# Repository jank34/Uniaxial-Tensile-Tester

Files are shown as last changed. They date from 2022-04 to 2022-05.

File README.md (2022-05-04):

# Uniaxial Tensile Tester
1. Repository Contents:

This repository contains the source code and libraries for the functionality of our tensiometer. Moreover, this repository also contains documentations on how to use the Tensiometer, the links on where to buy specific parts used in our Tensiometer, and 3D models for the clamps used in our design.

2. System Parts:

Part 1: Ultrasonic Range Sensor HR-SR04 $4- https://www.adafruit.com/product/4007?gclid=CjwKCAjwsJ6TBhAIEiwAfl4TWK9nOFg9-LFgLM61nsgyrghF30-v_zp0_7Xuo74gRQpIhaaqX7Zv8hoCigkQAvD_BwE

Part 2: Load Cell 20kg SEN-14729 $4- https://www.adafruit.com/product/4543

Part 3: Amplifier HX711 $2.10- https://www.amazon.com/dp/B00XRRNCOO/ref=cm_sw_r_sms_api_glt_i_WRGSQCYD8AA2CNPMWQPD

Part 4: Microcontoller Ard. Uno $15- https://www.amazon.com/Arduino-A000066-ARDUINO-UNO-R3/dp/B008GRTSV6/ref=asc_df_B008GRTSV6/?tag=hyprod-20&linkCode=df0&hvadid=309751315916&hvpos=&hvnetw=g&hvrand=6527864430974582771&hvpone=&hvptwo=&hvqmt=&hvdev=c&hvdvcmdl=&hvlocint=&hvlocphy=1022672&hvtargid=pla-457497319401&psc=1&tag=&ref=&adgrpid=67183599252&hvpone=&hvptwo=&hvadid=309751315916&hvpos=&hvnetw=g&hvrand=6527864430974582771&hvqmt=&hvdev=c&hvdvcmdl=&hvlocint=&hvlocphy=1022672&hvtargid=pla-457497319401

Part 5: LCD Screen With I2C TWI 1602 LCD $5 (pack of 2)- https://www.amazon.com/SunFounder-Serial-Module-Display-Arduino/dp/B019K5X53O/ref=asc_df_B019K5X53O/tag=hyprod-20&linkCode=df0&hvadid=312760964359&hvpos=&hvnetw=g&hvrand=703658664021823897&hvpone=&hvptwo=&hvqmt=&hvdev=c&hvdvcmdl=&hvlocint=&hvlocphy=1022672&hvtargid=pla-563014027379&psc=1

Part 6: Ratchet Crank Crank $26- https://www.amazon.com/CURT-29423-Manual-Trailer-Capacity/dp/B00TU7KME8/ref=sr_1_1?crid=5FC2MYGSWBAJ&keywords=curt+crank&qid=1651167054&s=industrial&sprefix=curt+crank%2Cindustrial%2C47&sr=1-1

Part 7: Pulleys $24- https://www.amazon.com/Chiloskit-Bearing-Bearings-Lifting-Triangular/dp/B07W1X5LTQ/ref=sr_1_25?crid=KAOX3XFYAL91&keywords=mounted%2Bpulley&qid=1651167187&sprefix=mounted%2Bpulley%2Caps%2C69&sr=8-25&th=1

Part 8: 6 feet Metal Cable $2- https://selkirkmetals.com/products/16-gauge-stainless-steel-rebar-tie-wire/?attribute_size=1+lb+Coil+(USA)+%5B304+Grade%5D+%5BQuantity%3A+1%5D&gclid=Cj0KCQjwyMiTBhDKARIsAAJ-9VuQNZg25S4BjEAm6hNkfRDY8u8t7IPsF_znqv66WN3v-eRoYqYu2UMaAg69EALw_wcB

3. Software Dependencies: 

Special libraries for codes in the library folder in the repository.

4. 3D Models:

Misc file contains 3D models of the clamps used in the project.

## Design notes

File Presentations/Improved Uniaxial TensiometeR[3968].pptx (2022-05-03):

## Improved Uniaxial TensiometeR

## Key components

- Ratchet Crank
- Pulleys
- Metal Rope
- LCD Screen
- 3D Printed Clamps

## Advantages of the system

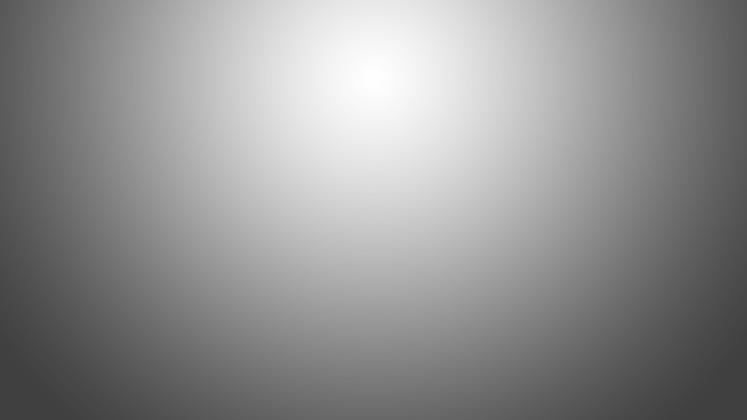
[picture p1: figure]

- Cost effectiveness.
- User friendly.
- Easily Replaceable parts.
- Easy Calibration process
- Accurate and Reliable results.

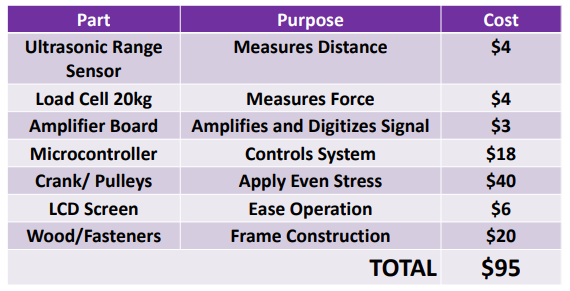
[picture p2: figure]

## System evolution

Initial Design and Results:

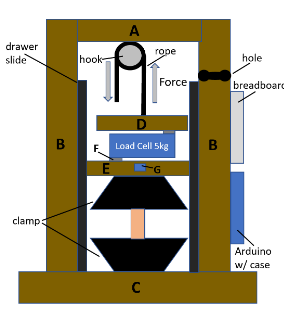
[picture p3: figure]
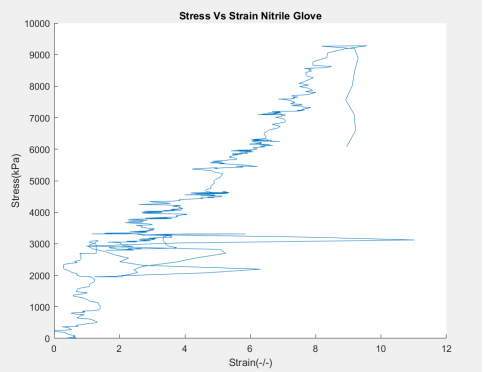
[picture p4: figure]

## System evolution

Modified Design and Results:

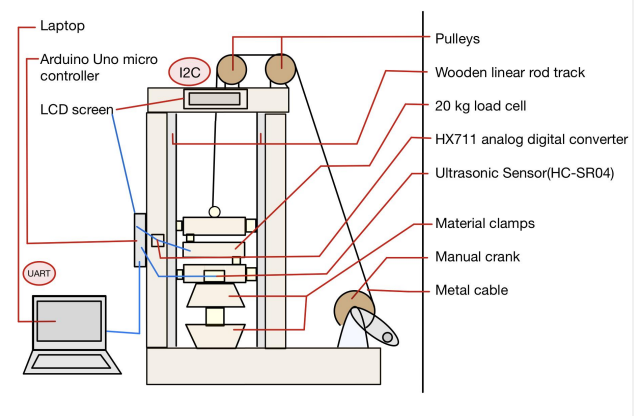
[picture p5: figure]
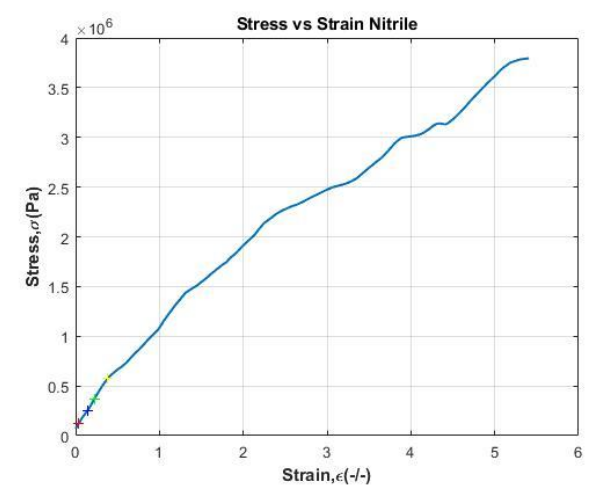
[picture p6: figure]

## Evolution

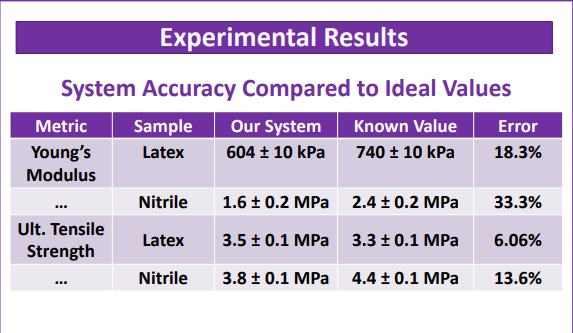
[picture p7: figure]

## Avenues for improvement

- Data Analysis that does not depend on MATLAB
- Additional 3D printed components
- Data retrieval independent of computer connection
- Smaller footprint
- Better sensors
- Taller linear track for more elastic materials

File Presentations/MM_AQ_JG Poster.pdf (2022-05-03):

# Improved Tensiometer

## Abdullah Qureshi, Jan Galia, Max Manier

### Department of Electrical & Computer Engineering, University at Albany

### Problem Statement

- The University at Albany’s chemistry department, as part of their educational mission, intends to build a laboratory for undergraduate students where they can gain hands on experience testing various material properties (including tensile strength). However, due to the extremely high cost of commercial products they have been unable to equip such a laboratory.
- The goal of this project is to build an accurate, low cost, easy to use uniaxial tensile strength tester to support this educational mission.

### System Requirements

### Experimental Results

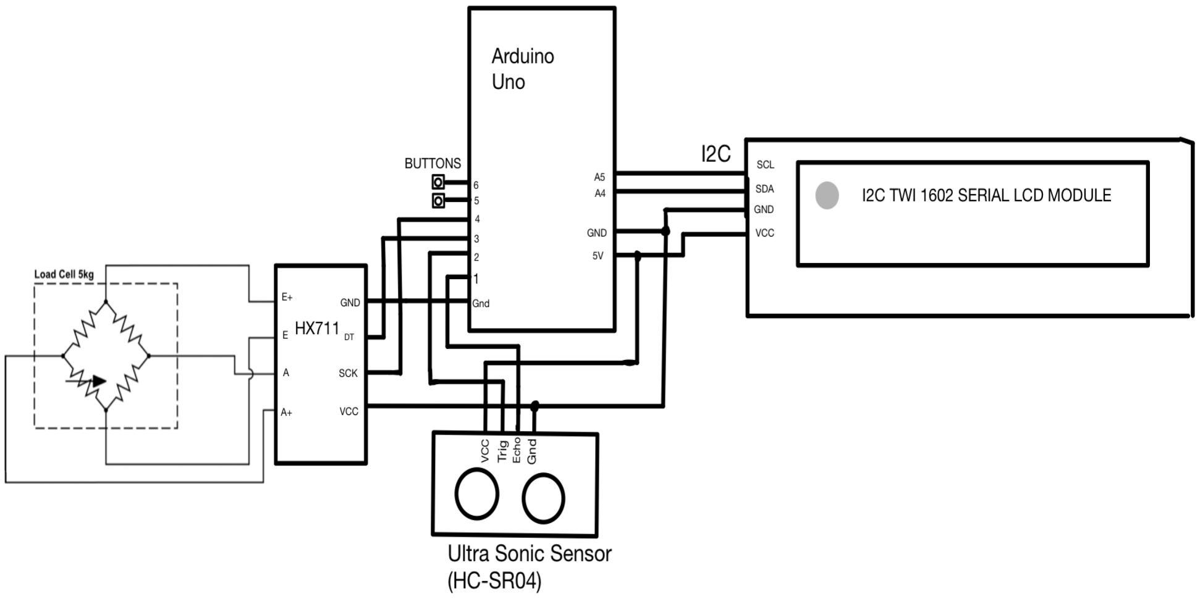
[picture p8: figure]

### Project Partners

### System Design

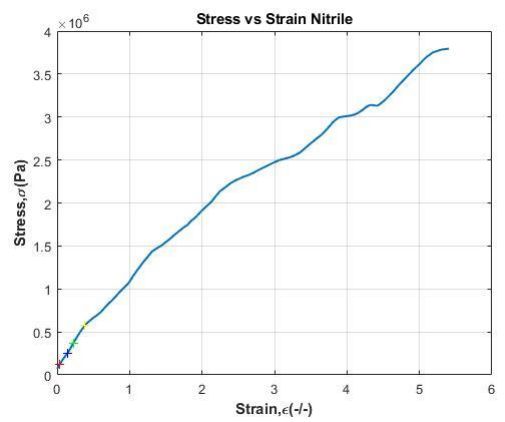
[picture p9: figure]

### System Components & Budget

Metric | Sample | Our System | Known Value | Error
Young’s Modulus | Latex | 604 ± 10 kPa | 740 ± 10 kPa | 18.3%
… | Nitrile | 1.6 ± 0.2 MPa | 2.4 ± 0.2 MPa | 33.3%
Ult. Tensile Strength | Latex | 3.5 ± 0.1 MPa | 3.3 ± 0.1 MPa | 6.06%
… | Nitrile | 3.8 ± 0.1 MPa | 4.4 ± 0.1 MPa | 13.6%
Part | Purpose | Cost
Ultrasonic Range Sensor | Measures Distance | $4
Load Cell 20kg | Measures Force | $4
Amplifier Board | Amplifies and Digitizes Signal | $3
Microcontroller | Controls System | $18
Crank/ Pulleys | Apply Even Stress | $40
LCD Screen | Ease Operation | $6
Wood/Fasteners | Frame Construction | $20
TOTAL | | $95

System Accuracy Compared to Ideal Values

Stress-Strain Curve Produced by Our Tensiometer
- System Accuracy: The system should be able to accurately measure the stress-strain curve, such that Young’s Modulus and Ultimate Tensile Strength can be calculated to within two significant figures.
- System Ease-of-Use: The system should be easy to calibrate and operate by undergraduate students without requiring knowledge of electronics or software programming.

Key System Features
The following features were implemented to satisfy the system requirements:
- Item #1: Inexpensive linear guide rail
- Item #2: Hand crank and pulleys to apply uniform force
- Item #3: LCD screen to provide clear information and useful instructions
- Item #4: Durable design using sturdy materials and manual components
- Item #5: Intuitive easy to use material clamps

Physical Model

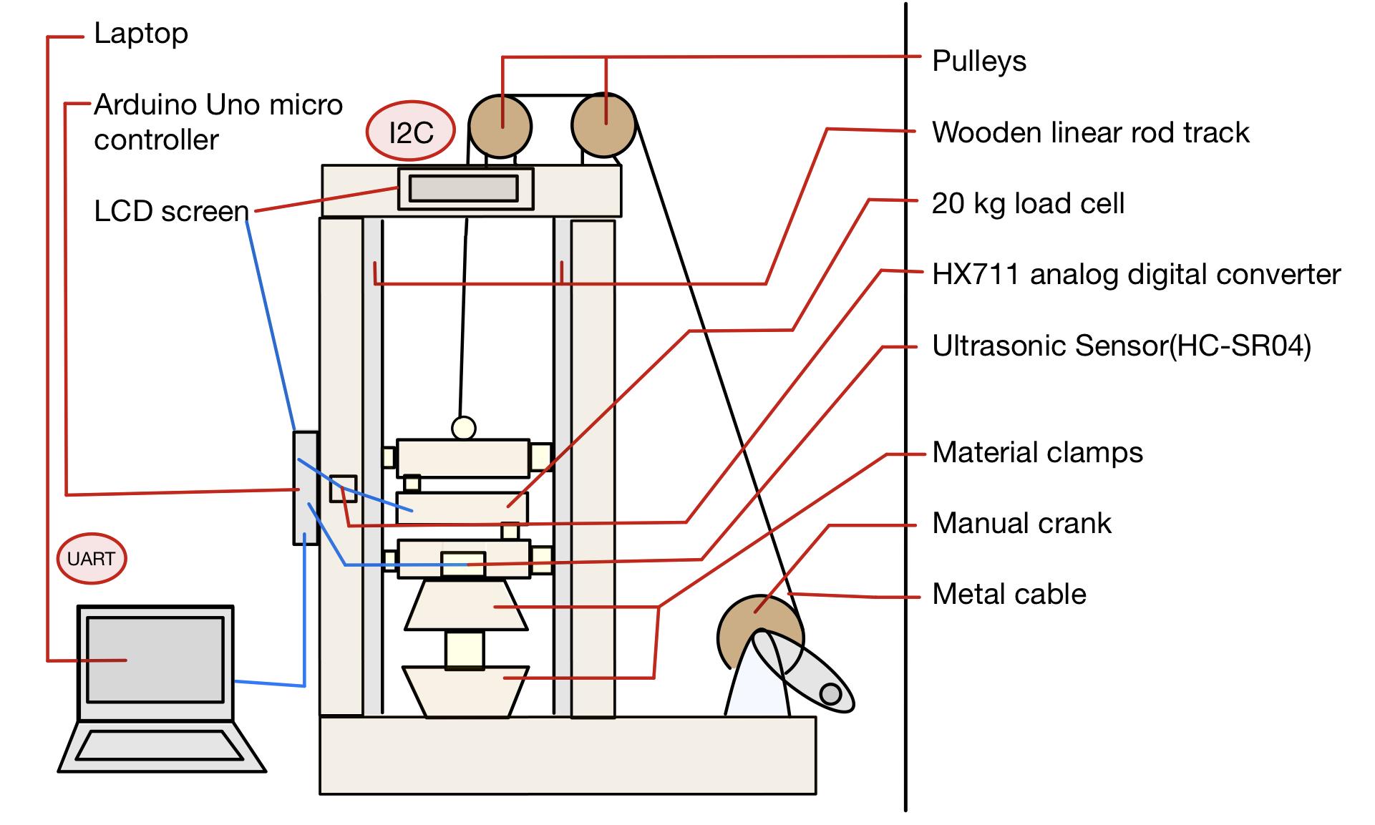
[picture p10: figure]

Circuit Schematic

- Special thanks for Professor Chen, Feldblyun, Yeung, and the University at Albany’s Chemistry Department for sponsoring this project.
- This project was developed in ECE442: Systems Analysis & Design in the Electrical & Computer Engineering Department.

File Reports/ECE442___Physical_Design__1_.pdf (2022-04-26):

PP-2017 V2.1

PHYSICAL DESIGN | 1

# Physical Design Proposal Team 2

Jan Karl Galia, Abdullah Qureshi, Max Manier

Activity Report

✦

### 1 PROPOSED SOLUTION

The proposed design is simplistic in nature and follows the designs constraints. The system consists of sturdy wooden frame and uses two pulleys to efficiently transfer force from an adjacent crank to apply a vertical load. The lower clamp is attached to the base and the upper clamp is attached to the shuttle with the load cell. The material under observation will be placed between these clamps. The laser sensor attached to the shuttle will measure the distance from the base as the rope is pulled through the pulley. The data will be read by both the load sensor and range sensor through micro-controller and processed accordingly. The LCD screen will display commands to help the calibration process and operation of the device. Commands can range from calibration instructions to operation instructions like ”Pull” or ”Stop”.

### 2 SYSTEM ARCHITECTURE

The main focus of the proposed design is to add a crank in order to apply a vertical load. In order to add a crank two pulleys have to be added on top of the device in order to have a linear and uniform pulling force on the shuttle.

- Jan Karl Galia,
E-mail: jgalia@albany.edu,
- Abdullah Qureshi,
E-mail: aqureshi@albany.edu,
- Max Manier,
E-mail: mmanier@albany.edu, University at Albany.

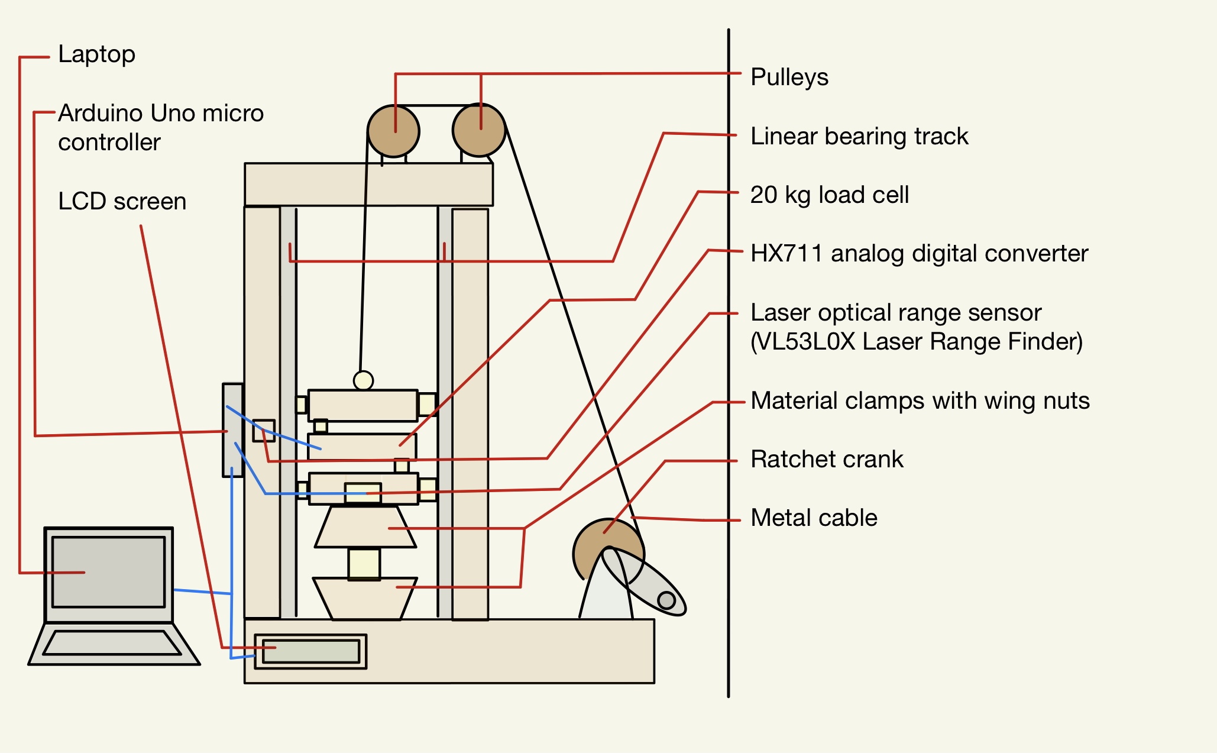
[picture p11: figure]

Figure 1. Current state of the tensiometer physical design.

Figure 1 depicts the current system physical design with a crank for applying a vertical load, and pulleys for linear force implementation on shuttle. The system also consists of LCD screen in order to aid in the calibration process and provide user with operation instructions.
The addition of the LCD screen will change the circuitry of the system. Figure 2 depicts the current system circuitry with the load cell acting a wheatstone bridge and the resulting output voltage amplified to the range of the ADC. The HX711 board uses the amplifed value to perform a ADC conversion and then communicates the results using the I2C communication standard with the attached microcontroller. Figure 3 depicts Arduino and LCD schematic. The LCD screen also uses the I2C communication standard with the attached microcontroller in order to make circuitry and wire management easier. The LCD screen typically uses 16 pins to

Activity Report

2 | PHYSICAL DESIGN

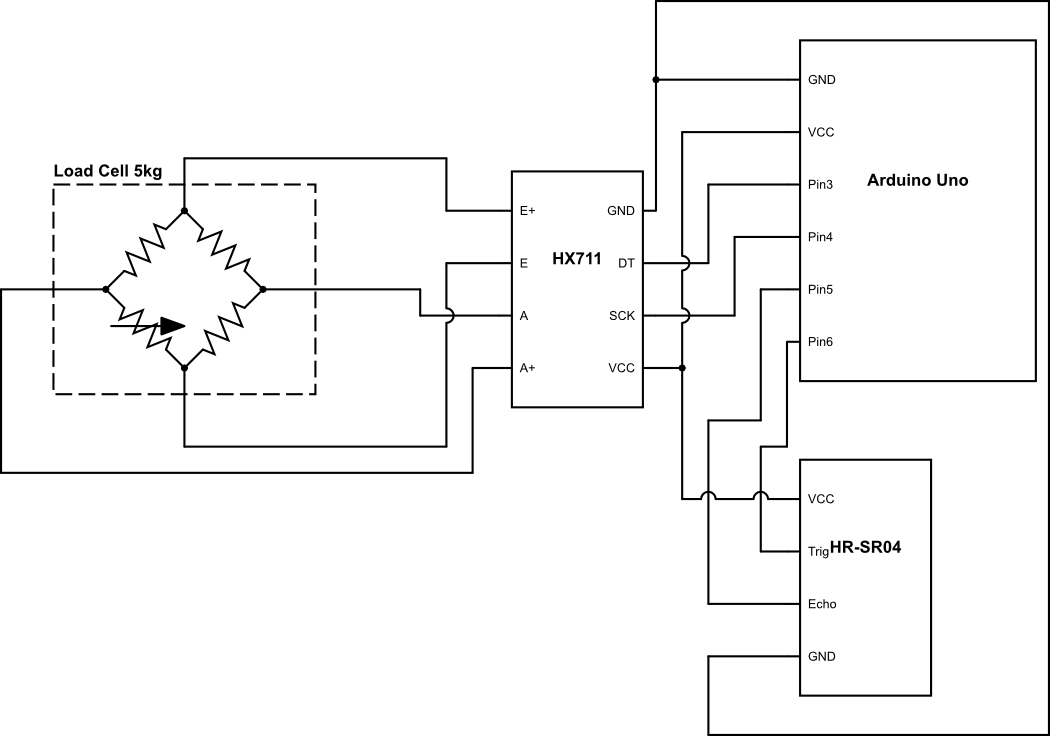
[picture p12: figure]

Figure 2. Schematic diagram of tensiometer electronics.

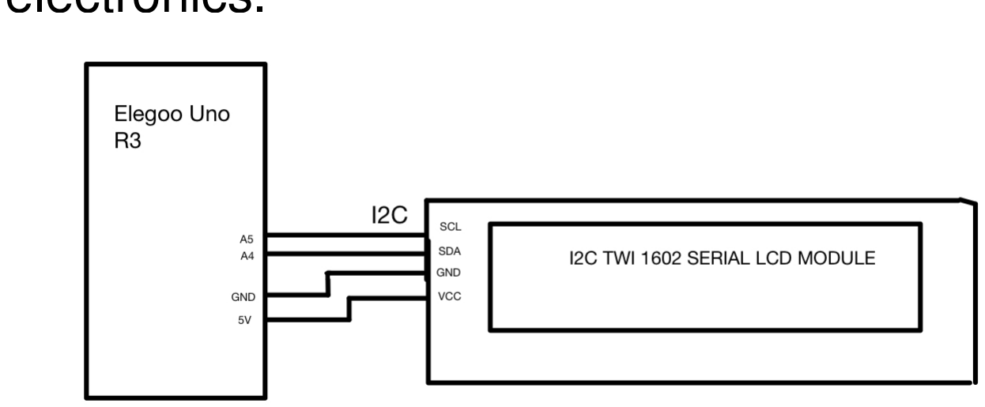
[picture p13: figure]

Figure 3. Schematic diagram of LCD screen With I2C.

work and display data on it, but by sing the I2C communication standard it can be reduced to 4 pins as shown in Figure 2. The LCD can work only by using pin VCC for power, SDA pin for data transmission, SCL pin for clock signal, GND pin for ground.

### 2.1 System Components

Some of the problems with the old system included non uniform application of force on the material under observation due to pulling the rope by hand. It was decided by the the team to use a Ratchet crank to pull the rope for uniform application of force, and because of its ability to stop the shuttle from returning to its original position. The following improvement has potential to greatly improve the accuracy, precision, and ease of use of the tensiometer. In order to have the crank apply linear force it was decided by the team to add pulleys onto the system. Another problem with the old system included the elasticity of the rope being used. It was decided by the team to replace that

Item | Part # | Cost
Ultrasonic Range Sensor | HR-SR04 | $4
Load Cell 20kg | SEN-14729 | $12
Amplifier | HX711 | $10
Microcontoller | Ard. Uno | $15
LCD Screen With I2C | TWI 1602 LCD | $5
Ratchet Crank | Crank | $20
Pulleys | Pulley | $20
Metal Cable | Cable | $3
TOTAL | | $89
Table 1
Table 1 displays an overview of parts purchased and their estimated price.

with a metal cable to reduce uncertainty in the data collection. Moreover, in order to reduce human error the team decided to use an LCD to display commands to help with the calibration process and operation of the device. Following are the new components of the system.

2.1.1 Ratchet Crank

The Ratchet Crank allows a user to apply uniform force on the material being stretched, and enables the user to stop the shuttle from going back to its original position without the need of force being applied from the user.

2.1.2 Pulleys

Pulleys are used in order to make the crank apply linear force on the material being stretched, and enables smooth pulling mechanism because of reduction in friction.

2.1.3 Metal Cable

The Metal Cable has negligible elasticity which reduces the errors and uncertainties in the data collected and the final result of Young’s Modulus and Ultimate Tensile Strength.

2.1.4 LCD Screen with I2C

The LCD screen will display commands to help the calibration process and operation of the device. Commands can range from calibration instructions to operation instructions like ”Pull” or ”Stop”.

PP-2017 V2.1

SURNAME et al. | 3

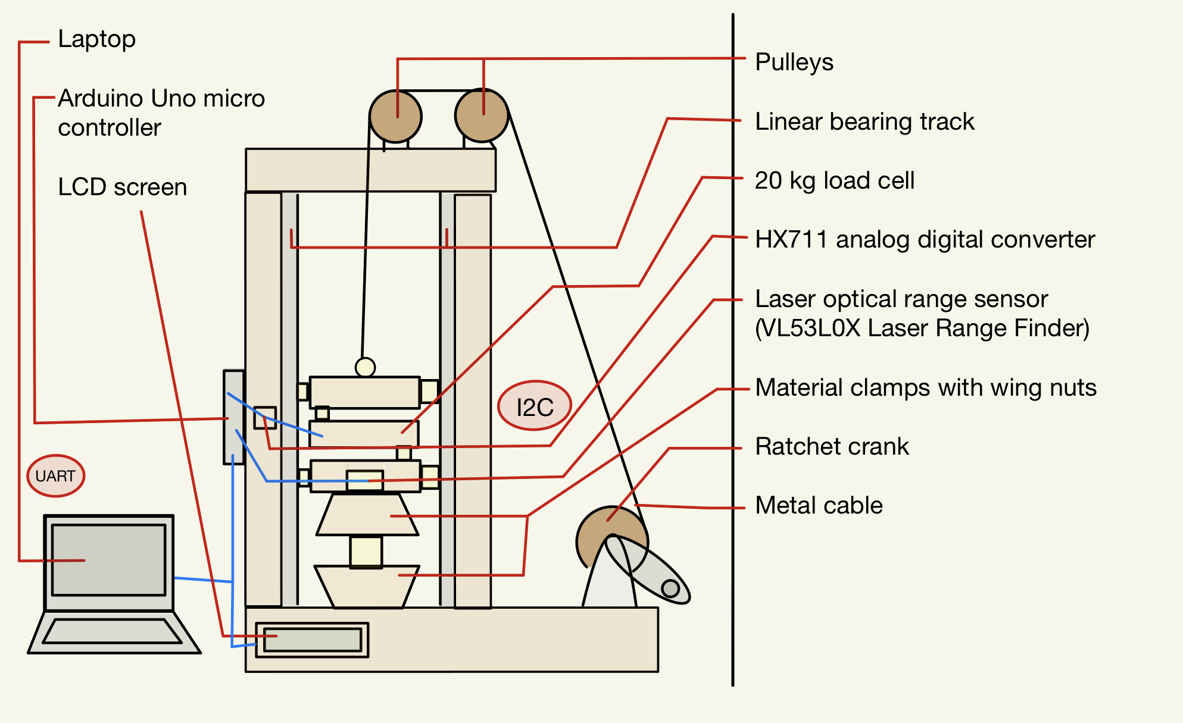
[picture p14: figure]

Figure 4. The current tensiometer system implements two communication standards (protocol) I2C and UART.

### 2.2 Engineering Standards

The current system utilizes I2C and UART protocols. I2C protocol is a serial communication protocol in which data is transferred bit by bit along a single wire (the SDA line). UART stands for Universal Asynchronous Receiver/Transmitter. It’s not a communication protocol like I2C, but a physical circuit in a microcontroller. A UART’s main purpose is to transmit and receive serial data.

2.2.1 I2C Protocol
I2C uses two wires to transmit data between devices. The current Tensiometer design uses Arduiono Uno which contains only one SCL (Pin 5) and SDA (Pin 4) pin. These same pins are connected to HX711, HR-SR04, and LCD screen. The SDA pin sends and receives data to and from the sensors and the LCD screen. SCK pin only sends a clock signal to the sensors and LCD screen to indicate data transmission and completion in data transmission.

2.2.2 UART Protocol
The main purpose of UART protocol is to send and receive data. The current Tensiometer design uses Arduino Uno which uses UART protocol to transmit and receive data to and from user’s laptop. In order for the communication to work the user must set the baud rate in the code. Any speed up to 115200 baud is viable but current code uses 9600 baud speed.

2.2.3 Data Standards
The current Tensiometer design uses Ardu Plotter tool in order to upload data calculated from the load cell and distance sensor to a CSV file. The data form CSV file is then uploaded to Matlab for creating stress vs strain curve, and calculate Young’s Modulus and Ultimate Tensile Strength.

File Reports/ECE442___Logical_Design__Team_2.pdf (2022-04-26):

PP-2017 V2.1

ANALYSIS & LOGICAL DESIGN | 1

# Uniaxial Tensile Tester Team 2

Jan Karl F. Galia, Max J. Manier, Abdullah A. Qureshi

Activity Report

Abstract—Among the problems with the current tensiometer design are accuracy of the range sensor, friction between the track, weight limit of the load cell, elasticity of the cable for pulling, human error when pulling, and non-uniform force application. The problems described above need to be addressed because they add errors to the measurements, making it difficult to calculate Young’s Modulus and Ultimate Tensile Strength accurately. The fixes for these problems include: Replacing the current range sensor with a laser optical range sensor for relatively accurate measurements of strain. Replacing the current load cell with a 20-kilogram load cell allows greater force application when stressing materials with large Young’s Modulus. Replacing the current pulling track with a linear bearing track reduces measurement errors caused by resistance. Replacing current cable with non elastic metal cable reduces errors in measurements caused by rope elasticity. Adding a ratchet crank in order to apply force uniformly. Lastly, adding a LCD screen to prompt the users with basic instructions improves ease of use. These solutions will allow for the stress and strain to be measured with greater accuracy and consistency.

Index Terms—Uniaxial Tensiometer, System Analysis, Engineering Design

✦

### 1 BACKGROUND

A tensiometer tests the strength and elasticity of a material by applying stress and observing how the material stretches, deforms, and eventually breaks. In order to accurately measure these variables both a load cell that measures the force applied, and a range sensor to find the amount the material stretches are necessary. It is essential that these sensors be calibrated and that the system allows for uniform and steady application of force. Any significant deviation of values will result in an inaccurate representation of material properties. The operation of this device should be relatively easy to learn and consistent in its performance regardless of the operator.
The current prototype [1] has several problem areas that have been identified. The range
- Jan Karl Galia,
E-mail: jgalia@albany.edu,
- Max Manier,
E-mail: mmanier@albany.edu,
- Abdullah Qureshi,
E-mail: aqureshi@albany.edu, University at Albany.

sensor is unreliable, it often produces inaccurate or even random values. There is significant friction between the track and shuttle which produces additional stress on the load sensor thereby inflating stress values. The weight limit of the load cell is fairly limited and will not allow for the testing of stronger materials. There is elasticity in the rope used to apply force and its own tensile properties could impact measurements. Testing has shown high potential for human error when applying force. The operator can easily unintentionally apply force at an uneven rate or even reduce force applied. The current system does not allow for a uniform increase in application of force. Lastly the code is cumbersome to use, especially for those unfamiliar with basic programming.
In order to improve upon the design several components will be replaced and some components will be added. The range sensor can be replaced with a laser range sensor rated for a higher degree of accuracy. The current track is a drawer slider and replacing it with a guide rail that uses bearings could reduce friction and weight of the shuttle. The load cell can be replaced with a 20kg load cell with the

Activity Report

2 | ANALYSIS & LOGICAL DESIGN

same dimensions. Instead of using a rope to
apply stress, a metal cable’s tensile properties
would be negligible at these weights. To provide smoother application of force the cable will be run over a pulley to a ratchet crank. Including a LCD screen with instructions can ease use of the device and reduce human error. None of these inclusions are expensive and their costs are comparable to the parts they replace. These modifications however have the potential to greatly increase the overall performance of the system by reducing the errors in measurement of Young’s Modulus and Ultimate Tensile Strength of the material being tested. Making the system more accurate and reliable is essential for the desired functionality of the Stakeholder. The proposed modifications will also make the operation of the devices easier which ultimately helps in operation and consistency of results.

### 2 SYSTEM REQUIREMENTS & CON-

STRAINTS
In order to define requirements it is important to understand what the stakeholder wants. The first major requirement is that the measurement of Young’s Modulus and Ultimate Tensile Strength is relatively equal to the theoretical value, and the system should be able to perform the task with consistency. The second major requirement is that the data collecting components of the system have the ability to be calibrated in order to get accurate and precise measurements for different materials. Calibration also assures similar reliable results across different devices.

### 2.1 Accuracy and Precision

The ”Run Tensile Test” use case aligns with this requirement. The desired functionality of this requirement is to get accurate and precise measurement of stress applied to the material under observation and strain produced in the material due to the application of stress. In order to start, the user will upload the Arduino code and open Ardu Plotter tool from the tools tab. The Ardu Plotter will give the distance of the sensor from the base and the amount of force applied on the material being stretched. The user will use the crank to pull the material until the material breaks. The Ardu Plotter tool will upload the data to an excel sheet which the user will use to plot stress vs. strain curve. Normal Flow
- Step #1: User Loads material to be tested into the clamps and increases tension until material is just taught, but not stressed.
- Step #2: User slowly cranks pulley when LCD displays ”GO”, straining the material.
- Step #3: System records displacement and force every 0.5 seconds.
- Step #4: User stops cranking the rope after the material fractures, can not be displaced further, or LCD displays ”STOP”.
- Step #5: Chemist analyzes the data. Stress is calculated by dividing force by crosssectional area. Stress-strain curve is defined. Material properties are determined. Alternative Flow
- Step #1: User slowly cranks pulley when LCD displays ”GO”, straining the material
- Step #2: Ultimate tensile strength of the material is beyond load cell limits. When load cell approaches 75 percent of maximum load, LEDs flash, and LCD displays warning message.
- Step #3: User stops cranking the rope after the material fractures, can not be displaced further, or LCD displays ”STOP”

### 2.2 Calibration

The ”Calibrate Instrument” use case aligns with this requirement. The desired functionality of this requirement is to calibrate the load cell and the range sensor to get accurate measurement of the force applied on the load cell due to pulling the rope and and strain produced in the material due to application of stress. In order to start the calibration, the user will upload the Arduino code which will prompt the user to put a known load on the load cell and prompt the user to type in raw value of load cell. The code will then generate a calibration value and calibrate the load cell to give an accurate measurement of the load. Normal Flow

PP-2017 V2.1

SURNAME et al. | 3

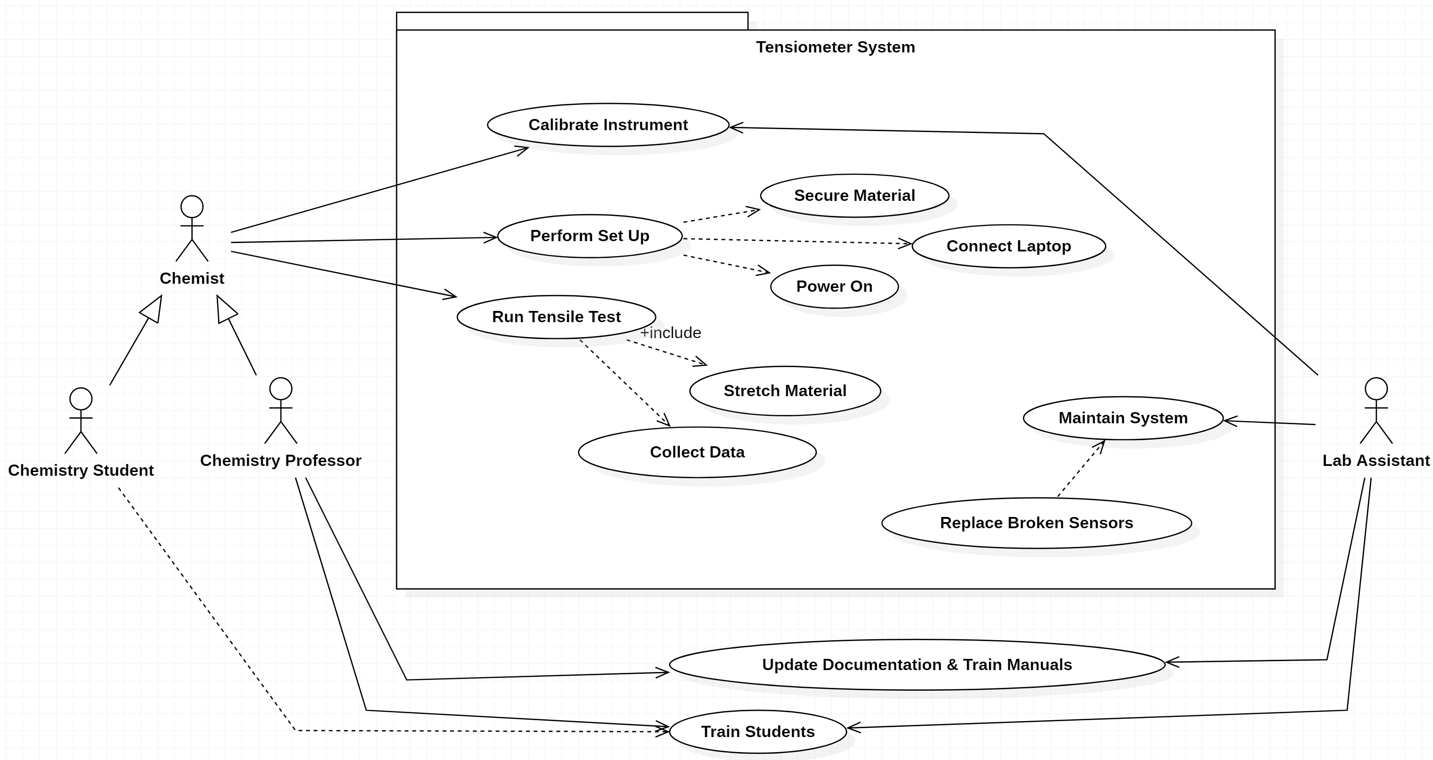
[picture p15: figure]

Figure 1. Use case model of the tensiometer system depicting system actors and the desire actions the system is required to support.

- Step #1: User will upload the Arduino
Code.
- Step #2: Code will prompt the user to put a known load cell.
- Step #3: Code will prompt the user to write the mass of load.
- Step #4: The load cell gets calibrated and the user gets accurate and reliable measurement.
Alternative Flow
- Step #1: User will upload the code.
- Step #2: Code will prompt the user to put a known load cell.
- Step #3: If calibration fails LCD displays warning message.
- Step #4:User re-uploads the code and calibration runs again.

### 2.3 Constraints

System constraints include:
- Time Constraint: Completed and read to presentation/demonstrate by April 22nd
- Budget: Cost needs to be below $150. Going over budget will require strong justification as to the value added from the cost overrun.
- Replication: Relatively straight-forward process to replicate your work, such that we can build out a lab of identical tensiometers.
- Accessibility of Parts: Parts need to be readily accessible, ship quickly (not on back order) and available from common part suppliers (e.g., Digikey, Mouser, Adafruit, SparkFun, Amazon). Avoid parts that are difficult to source.
- Safety: System must be safe to operate without significant training or supervision

### 3 LOGICAL DESIGN

The proposed design is simplistic in nature and follows the designs constraints. Referencing the Figure 2, the system consists of sturdy wooden frame and uses two pulleys to efficiently transfer force from an adjacent crank to apply a vertical load. The lower clamp is attached to the base and the upper clamp is attached to the shuttle with the load cell. The material under observation will be placed between these

Activity Report

4 | ANALYSIS & LOGICAL DESIGN


Figure 2. Uniaxial Tensile Tester Design

clamps. The laser sensor attached to the shuttle will measure the distance from the base as the rope is pulled through the pulley. The data will be read by both the load sensor and range sensor through micro-controller and processed accordingly. The LCD screen will display commands to help the calibration process and operation of the device. Commands can range from calibration instructions to operation instructions like ”Pull” or ”Stop”.

### 3.1 Design Justification

This design is better than potential alternatives because of its ability to increase the load uniformly, low friction linear bearing tracks, higher load capacity, useful LCD screen, and easy-to-use clamps. This design allows for intuitive operation and accurate values. The current system is cumbersome to use and does not provide accurate and precise measurements of stress and strain. These shortfalls will impede the users ability to find Young’s Modulus and Ultimate Tensile Strength of the material under observation. The advancements stated above will increase the accuracy and precision of measurements by reducing systematic and human errors.

REFERENCES

[1] J. H. Arrizabalaga, A. D. Simmons, and M. U. Nollert, “Fabrication of an economical arduino-based uniaxial tensile tester,” Journal of Chemical Education, vol. 94, no. 4, pp. 530–533, 2017. [Online]. Available: https: //doi.org/10.1021/acs.jchemed.6b00639

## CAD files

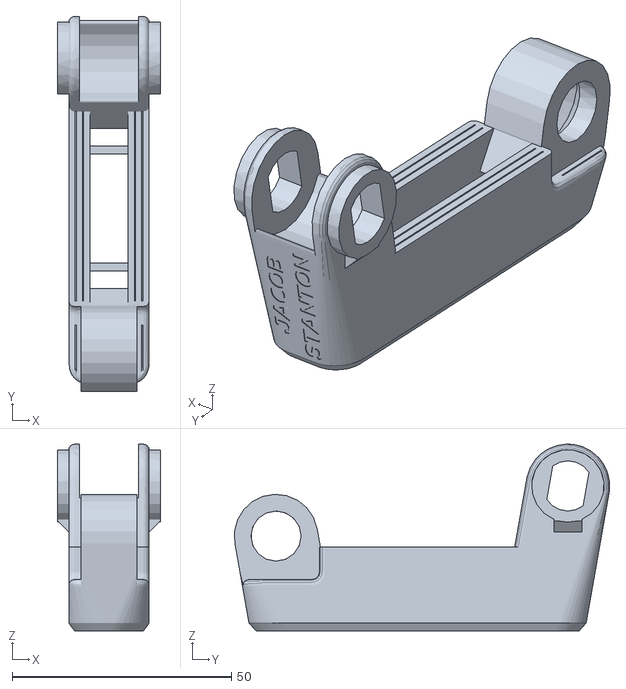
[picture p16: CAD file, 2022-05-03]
MISC/jawBottom(1).STL
23.4 x 85.4 x 42.5

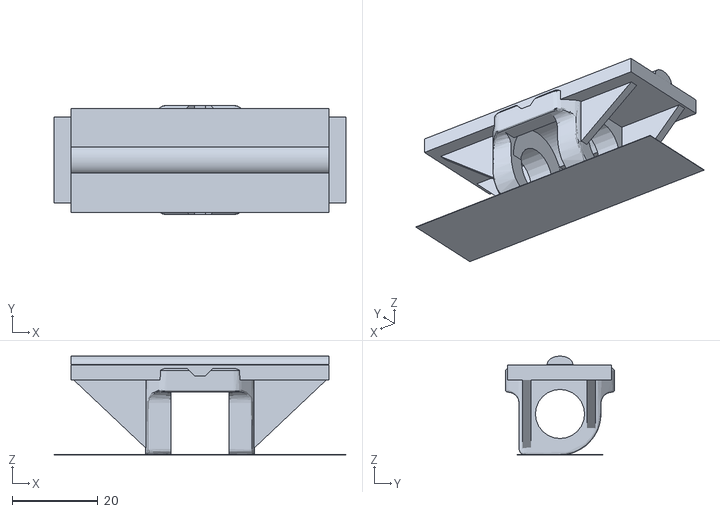
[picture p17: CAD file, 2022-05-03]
MISC/Pad Male(7).stl
68.0 x 25.4 x 23.0

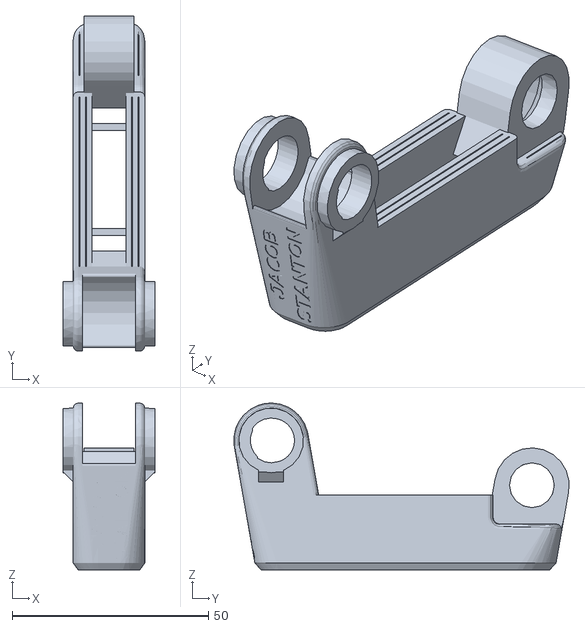
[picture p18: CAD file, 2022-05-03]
MISC/lower jaw(4).stl
23.4 x 85.4 x 42.5

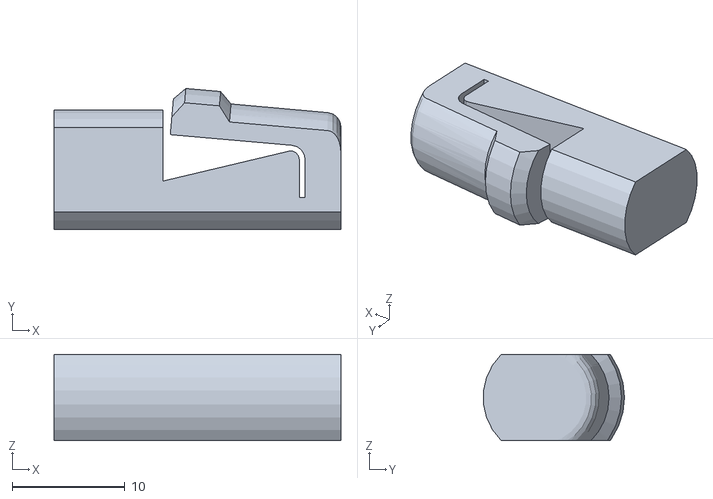
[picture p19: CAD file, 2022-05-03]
MISC/pin(8).STL
25.4 x 12.5 x 7.62

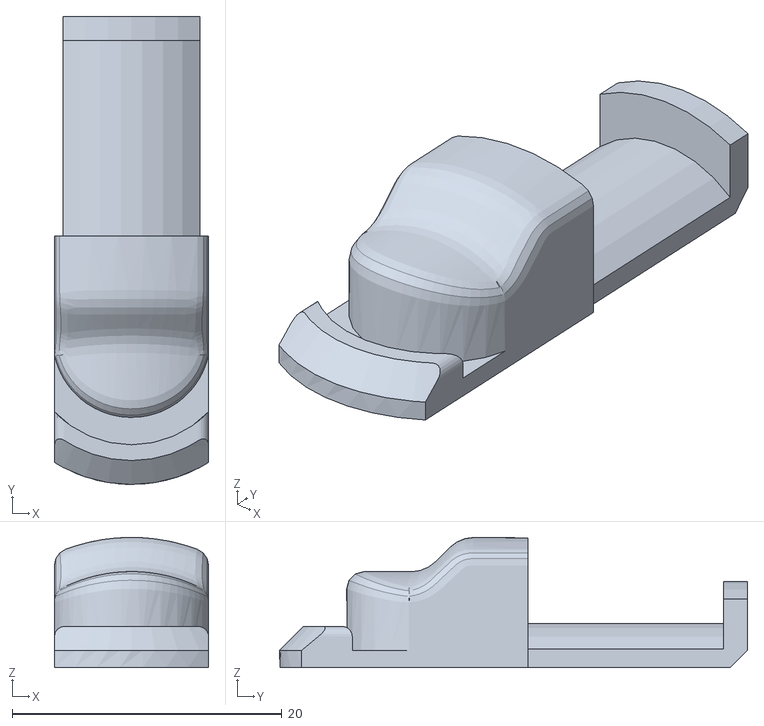
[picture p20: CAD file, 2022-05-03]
MISC/retainer(9).STL
11.4 x 34.7 x 9.65

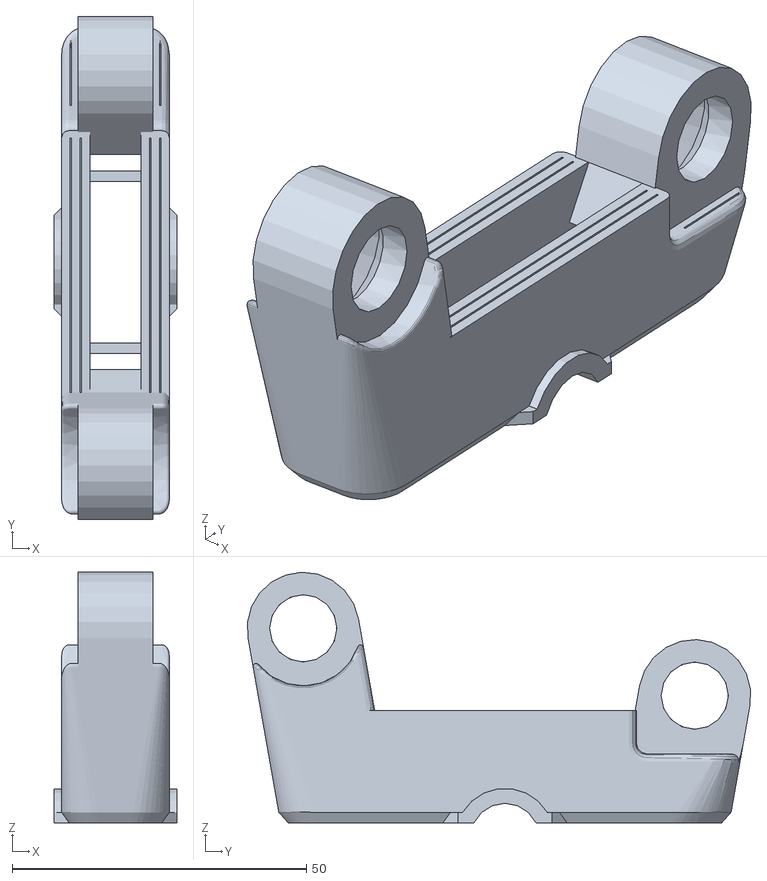
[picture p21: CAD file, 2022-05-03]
MISC/jawTop(2).STL
20.8 x 85.4 x 42.5

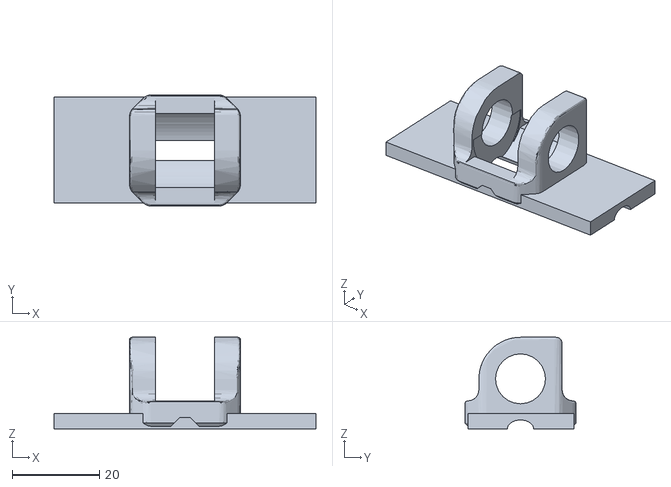
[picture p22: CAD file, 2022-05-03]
MISC/Pad female(6).stl
60.0 x 25.4 x 21.0

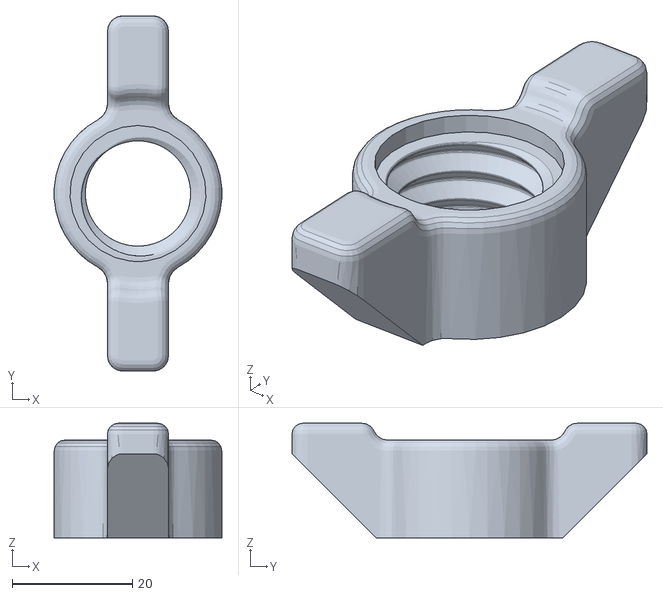
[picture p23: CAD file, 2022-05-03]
MISC/knob(3).STL
27.9 x 59.0 x 19.1

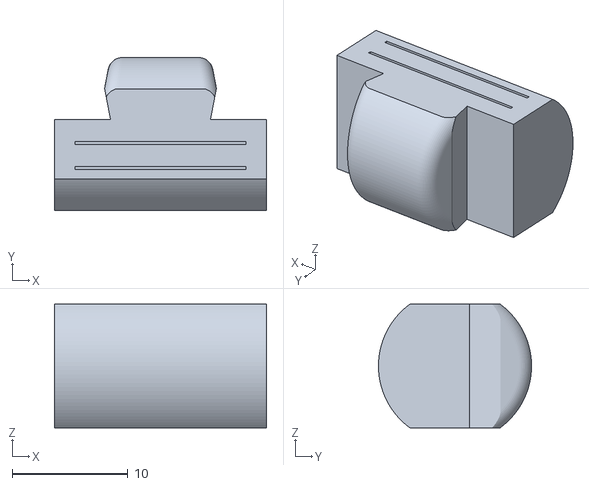
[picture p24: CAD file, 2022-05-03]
MISC/threadPin(10).STL
18.3 x 13.2 x 10.7

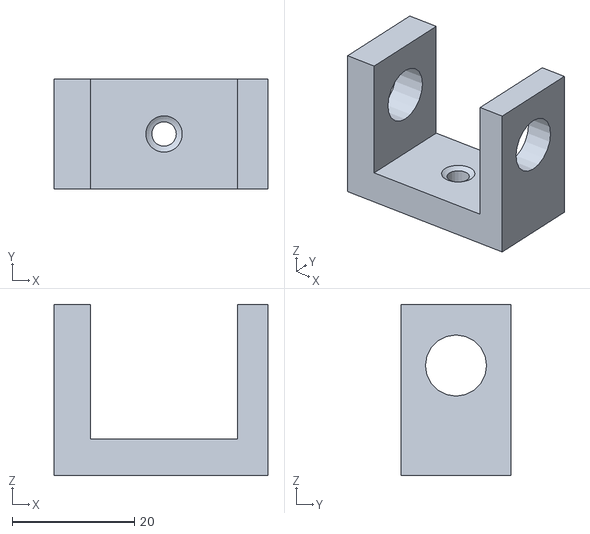
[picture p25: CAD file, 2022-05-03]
MISC/Mounting bracket(5).stl
35.0 x 18.0 x 28.0

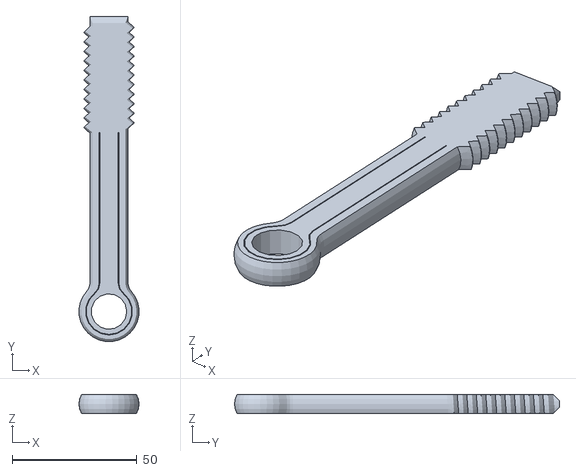
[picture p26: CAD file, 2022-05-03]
MISC/threads(11).STL
24.1 x 130.1 x 7.62

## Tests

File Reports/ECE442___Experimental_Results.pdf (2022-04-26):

PP-2017 V2.1

EXPERIMENTAL DESIGN | 1

# Uniaxial Tensiometer (Experimental Results)

Abdullah Qureshi, Jan Galia, Max Manier

Activity Report

✦

### 1 RESEARCH QUESTION

The primary goal of our improved uniaxial tensiometer system is to increase system accuracy by reducing friction in the system by using wooden linear rod track, and pulleys and crank system for uniform application of force. To demonstrate the accuracy of our system, we tested our system on two different types of material (latex and nitrile) and compared the values of Young’s modulus and ultimate tensile strength computed from the stress-strain curve to known values for these materials

### 2 EXPERIMENTAL RESULTS

1) Stress-strain curve for latex glove (See Figure 1).
2) Stress-strain curve for nirile glove (See Figure 2).
3) Table summarizing key metrics (See Table 2).
The referenced graph shows how material is stretched when pressure is applied on the material. The referenced table show the calculated Young’s Modulus and Ultimate Tensile Strength values. Young’s Modulus is the slope of the linear region of the graph. Ultimate Tensile Strength is the maximum value of stress the material can withstand before breaking.
- Abdullah Qureshi. 12222,
E-mail: aqureshi@albany.edu,
- Max Manier. 12222,
E-mail: mmanier@albany.edu,
Electrical & Computer Engineering, University at Albany.

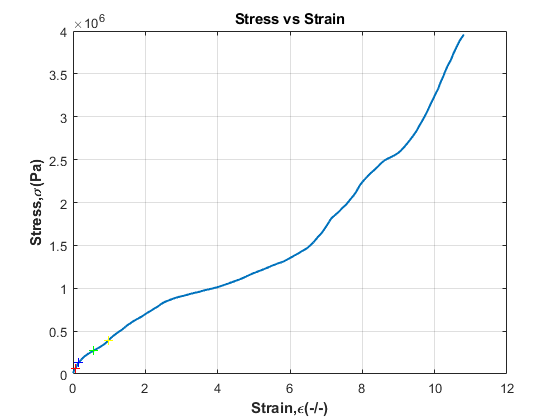
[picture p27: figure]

Figure 1. Stress-strain curve derived from our system for Latex glove sample

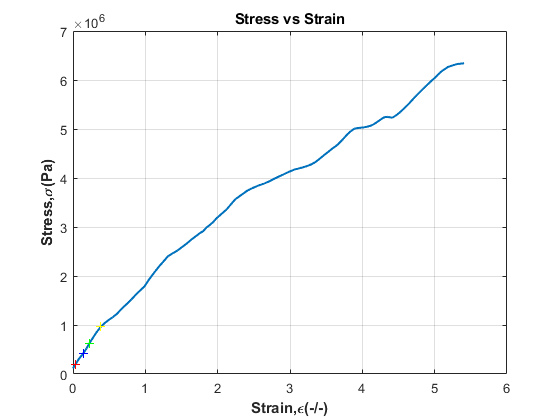
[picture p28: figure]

Figure 2. Stress-strain curve derived from our system for nitrile glove sample

Activity Report

2 | EXPERIMENTAL DESIGN
Metric | Sample | # Trials | Our System | Known Value | Error
Young’s Modulus | Latex Glove | 1 | 604 ± 10 kPa | 740 ± 10 kPa | 18.3
.. | Nitrile Glove | 1 | 1.6 ± 0.2 MPa | 2.4 ± 0.2 MPa | 33.3
Ultimate Tensile Strength | Latex Glove | 1 | 3.5 ± 0.1 MPa | 3.3 ± 0.1 MPa | 6.06
.. | Nitrile Glove | 1 | 3.8 ± 0.1 MPa | 4.4 ± 0.1 MPa | 13.6
Table 1
Summary of experimental results from multiple trials
Metric | Sample | # Trials | Our System | Known Value | Error
Young’s Modulus | Latex | 2 | 632 ± 10 kPa | 740 ± 10 kPa | 14.6
.. | Nitrile | 2 | 1.92 ± 0.2 MPa | 2.4 ± 0.2 MPa | 20
Ult. Tensile Strength | Latex | 2 | 3.1 ± 0.1 MPa | 3.3 ± 0.1 MPa | 6.06
.. | Nitrile | 2 | 4.0 ± 0.1 MPa | 4.4 ± 0.1 MPa | 9.09
Table 2
Summary of experimental results from multiple trials

### 3 DATA ANALYSIS

As we can see from the results the difference between the observed and theoretical Young’s Modulus and Ultimate Tensile Strength is not that large. This indicates that our current system is very accurate. Similarly, when different trials were done the key metrics were overall consistent, thus indicating that our current system is reliable as well. One of the best practices in building an accurate and reliable tensiometer is to use a load cell and range sensor which is more accurate and which does not through random values while being tested.

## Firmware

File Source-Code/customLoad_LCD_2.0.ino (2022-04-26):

#include "HX711.h"
#include <EEPROM.h>
#include <LiquidCrystal_I2C.h>

#define echoPin 2
#define trigPin 3

const int LOADCELL_DATA_PIN = 4;
const int LOADCELL_CLOCK_PIN = 5;

const int button1Pin = 6; // Button 1
const int button2Pin = 7; // Button 2

HX711 scale;


double knownVal = 1000; // known weight value used for calibration.
double tare = -28.77; // variable carries tare value for claibration
double duration; // variable for the duration of sound wave travel
double distance; // variable for the distance measurement
double rollDistance = 0; // variable used to find rolling average of distance
double rollLoad = 0; // variable used to find rolling average of load
double weight = 0.5; // weight used for rollLoad and rollDistance calculations.
double load; // variable carries running weight in grams
int calibrate = 0; // variable will hod 1 if user wants to calibrate, 0 if not.
double calibration = -0.1; // variable holds the running calibration value.
double tempLoad = 0; // variable will hold largest load value.
int button1State = 0; // variable will hold 1 if button 1 is pressed
int button2State = 0; // variable will hold 1 if button 2 is pressed

LiquidCrystal_I2C lcd(0x27, 20, 4);


void setup() {
  Serial.begin(9600);
  wantCalibration();
  pinMode(trigPin, OUTPUT);
  pinMode(echoPin, INPUT);
  scale.begin(LOADCELL_DATA_PIN, LOADCELL_CLOCK_PIN);

  digitalWrite(trigPin, LOW);
  delayMicroseconds(2);

  // Sets the trigPin HIGH (ACTIVE) for 10 microseconds
  digitalWrite(trigPin, HIGH);
  delayMicroseconds(10);
  digitalWrite(trigPin, LOW);

  // Reads the echoPin, returns the sound wave travel time in microseconds
  duration = pulseIn(echoPin, HIGH);

  // Calculating the distance
  rollDistance = duration * 0.034 / 2.0; // Speed of sound wave divided by 2 (go and back)


  // If user wants to calibrate run this block.
  if (calibrate == 1) {

    lcd.backlight();
    lcd.setCursor(0, 0);
    lcd.print("GettingTareValue");
    lcd.setCursor(0, 1);
    lcd.print("                ");
    delay(1000);

    tare = scale.read_average(20) / 100;

    lcd.backlight();
    lcd.setCursor(0, 0);
    lcd.print("Put 1kg on load cell");
    lcd.setCursor(0, 1);
    lcd.print("Then push button");
    int tempPress;
    tempPress =  buttonPress();

    load = (scale.read_average(20) / 100) - tare;

    calibration = load / knownVal;

    lcd.backlight();
    lcd.setCursor(0, 0);
    lcd.print("  Remove Weight ");
    lcd.setCursor(0, 1);
    lcd.print("Then push button");
    tempPress = buttonPress();

    lcd.setCursor(0, 0);
    lcd.print("                ");
    lcd.setCursor(0, 0);
    lcd.print("Calibration = ");
    lcd.setCursor(0, 1);
    lcd.print("                ");
    lcd.setCursor(0, 1);
    lcd.print(calibration);
    EEPROM.put(0, calibration);
    delay(1000);
    delay(1000);
    delay(1000);
    lcd.setCursor(0, 0);
    lcd.print("PutSampleInClamp");
    lcd.setCursor(0, 1);
    lcd.print("Press any button");
    tempPress = buttonPress();

    tare = scale.read_average(20) / 100;
  }
  // If user doesn't want to calibrate run this block.
  else {
    lcd.backlight();
    lcd.setCursor(0, 0);
    lcd.print("FetchingDataFrom");
    lcd.setCursor(0, 1);
    lcd.print("Memory          ");
    delay(1000);
    delay(1000);
    calibration = EEPROM.get(0, calibration);
    lcd.setCursor(0, 0);
    lcd.print("                ");
    lcd.setCursor(0, 0);
    lcd.print("Calibration =   ");
    lcd.setCursor(0, 1);
    lcd.print("                ");
    lcd.setCursor(0, 1);
    lcd.print(calibration);
    delay(1000);
    delay(1000);
    delay(1000);
    lcd.setCursor(0, 0);
    lcd.print("PutSampleInClamp");
    lcd.setCursor(0, 1);
    lcd.print("Press any button");
    int tempPress;
    tempPress = buttonPress();

    tare = scale.read_average(20) / 100;

  }
  rollLoad = ((scale.get_value() / 100) - tare) / calibration;

}

void loop() {
  // Check if calibration failed.
  if (checkCalibration() == false) {
    lcd.backlight();
    lcd.setCursor(0, 0);
    lcd.print("Calibration Fail");
    lcd.setCursor(0, 1);
    lcd.print("RunProgramAgain");
    redLed();
  }
  // If calibration is successful check for break.
  else {
    if (checkBreak() == false) {
      lcd.backlight();
      lcd.setCursor(0, 0);
      lcd.print(" Turn the crank ");
      lcd.setCursor(0, 1);
      lcd.print("     slowly      ");
      greenLed();
    }
    else {
      lcd.backlight();
      lcd.setCursor(0, 0);
      lcd.print(" Break Occurred ");
      lcd.setCursor(0, 1);
      lcd.print("      Stop      ");
      redLed();
    }
  }

  load = ((scale.get_value() / 100) - tare) / calibration;

  if ( load > tempLoad) {
    tempLoad = load;
  }

  double tempD;
  distance = 0;
  for (int i = 0; i < 10; i++) {
    digitalWrite(trigPin, LOW);
    delayMicroseconds(2);

    digitalWrite(trigPin, HIGH);
    delayMicroseconds(10);
    digitalWrite(trigPin, LOW);

    duration = pulseIn(echoPin, HIGH);

    tempD = duration * 0.034 / 2.0;
    distance = distance + tempD;
  }
  distance =  distance / 10;

  if (distance > rollDistance) {
    rollDistance = ((1.0 - weight) * rollDistance) + (weight * distance);
    rollLoad = ((1.0 - weight) * rollLoad) + (weight * load);

    Serial.print(rollLoad);
    Serial.print('\t');

    Serial.print(rollDistance);
    Serial.print('\t');

    Serial.println(tempLoad);

  }
}

// Function checks if user wants to calibrate
void wantCalibration() {
  lcd.init();
  lcd.backlight();
  lcd.setCursor(0, 0);
  lcd.print("Always Calibrate");
  lcd.setCursor(0, 1);
  lcd.print("On First Startup");
  delay(1000);
  delay(1000);
  lcd.setCursor(0, 0);
  lcd.print("B1:Calibrate    ");
  lcd.setCursor(0, 1);
  lcd.print("B2:No Calibrate ");
  int push = 0;
  push = buttonPress();

  // If user presses button 1, Calibrate is 1. If user presses button 2 , Calibrate is 0.
  if (push == 1) {
    calibrate = 1;
  }
  else {
    calibrate = 0;
  }
}

// Function checks if calibration was successsful.
bool checkCalibration() {
  if (calibration != 0) {
    return true;
  }
  else {
    return false;
  }
}

//Function checks if material broke.
bool checkBreak() {
  if (load < (0.25 * tempLoad)) {
    return true;
  }
  else {
    return false;
  }
}

// Function waits for user to either press button 1 or button 2.
int buttonPress() {
  while (button1State == 0 && button2State == 0) {
    button1State = digitalRead(button1Pin);
    button2State = digitalRead(button2Pin);
    if (button1State == HIGH) {
      button1State = 0;
      button2State = 0;
      return 1;
    }
    if (button2State == HIGH) {
      button1State = 0;
      button2State = 0;
      return 2;
    }
  }
}

// Function turns on Green LED and Turns off Red LED
void greenLed() {
  pinMode(8, OUTPUT);
  pinMode(9, OUTPUT);
  digitalWrite(8, HIGH);
  digitalWrite(9, LOW);
}

// Function turns on REd LED and Turns off Green LED
void redLed() {
  pinMode(8, OUTPUT);
  pinMode(9, OUTPUT);
  digitalWrite(9, HIGH);
  digitalWrite(8, LOW);
}
